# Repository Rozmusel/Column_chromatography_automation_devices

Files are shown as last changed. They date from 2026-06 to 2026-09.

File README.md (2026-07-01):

# Устройства автоматизации колоночной хроматографии
В настоящее время, хроматографический метод разделения веществ широко применим во многих научных лабораториях по всему миру. Одним из наиболее популярных видов является препаративная колоночная хроматография, активно использующаяся исследователями в области органической химии по сей день.
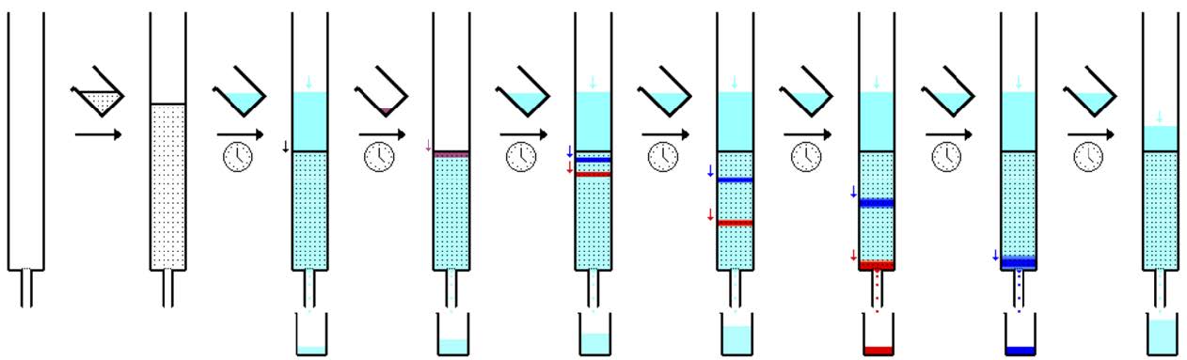
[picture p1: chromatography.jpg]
A1-4CCH

Интерес к данному методу выделения индивидуальных соединений из смеси не случаен – для его проведения нужны крайне дешевые расходные материалы (чаще всего силикагель или цеолит в качестве неподвижной фазы и этилацетат, гексан в качестве элюента) и недорогое стеклянное оборудование (колонка, пробирки или плоскодонные колбы). Более того, в результате прохождения смеси через колонку на выходе научный сотрудник получает продукт с чистотой до 99%.
Подбирая колонку нужного диаметра и регулируя толщину слоя твёрдого адсорбента, исследователь имеет возможность разделять смеси самой различной массы, что является важным преимуществом перед дорогостоящим оборудованием высокоэффективной жидкостной хроматографией (ВЭЖХ), в котором имеются ограничения по массе вводимого вещества. 
Однако существенным недостатком метода препаративной колоночной хроматографии является его длительное время проведение и непосредственное участие исследователя для замены заполненной колбы на пустую под колонкой. В зависимости от диаметра колонки и адсорбента каждая колба наполняется элюентом в среднем за 4-5 минуты, после чего её нужно менять вручную на новую. Так, научный сотрудник вынужден, откладывая проведение синтезов, следить за хроматографическим процессом.
Решением проблемы долгой ручной сортировки может стать устройство, которое умеет вовремя сменять колбы по мере их наполнения и желательно разделять по стекаемо фазе. Так как в лабораториях часто используют конические колбы объёмом 25 мл и 50 мл, то прибор должен уметь работать с ними.

Существующие решения весьма дорогие, потому исследовательские команды часто не могут позволить себе профессиональные ВЭЖХ или сортировщики фракций, моя задача - найти компромисс между качеством разделяемых смесей, удобством и разумной ценой.

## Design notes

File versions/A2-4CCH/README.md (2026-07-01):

# Прототип A2-4CCH
**Allocator for Column Chromatography v2**

## Назначение
* Решение проблемы небольшой вместимости прошлой версии устройства
* Повышение надёжности

## Статус
В процессе разработки.

## Конструкция
* XY стол на винтовой передаче.
* Привод - JGA25-370 DC gear motor.
* Управление на плате STM32G474CEU6 от WeAct.

## Средства разработки
### CAD
* Компас-3D v24

### Прошивка
* STM32CubeMX
* Visual Studio Code

## Результаты

## Выявленные недостатки

### Материалы

### Эксплуатационные испытания

## Основные выводы

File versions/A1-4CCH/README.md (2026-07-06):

# Прототип A1-4CCH
**Allocator for Column Chromatography v1**
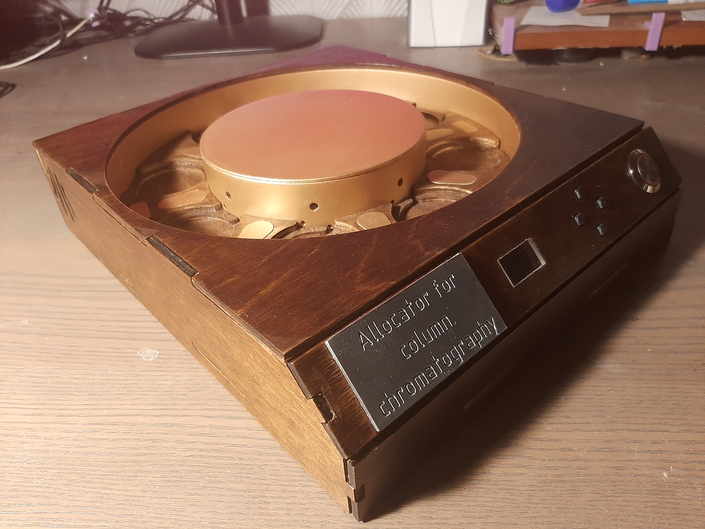
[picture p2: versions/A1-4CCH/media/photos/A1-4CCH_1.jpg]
A1-4CCH

## Назначение
Разработка устройства для автоматической смены колб под хроматографической колонкой по мере их наполнения.
## Статус
Завершён. Испытания проведены.
## Конструкция
* Карусельный механизм для размещения приёмных колб.
* Привод карусели — шаговый двигатель.
* Система управления построена на платформе Arduino.
* Определение наполненности колб лазером и фоторезистором.

## Средства разработки
### CAD
* Autodesk Inventor Professional 2024

### Прошивка
* Arduino IDE

## Результаты
* Разработано и изготовлено работоспособное устройство.
* Работоспособность подтверждена лабораторными испытаниями.
* Продемонстрирована возможность автоматической смены колб по мере их наполнения без участия оператора.
* Получен патент на метод определения наполненности колб.

## Выявленные недостатки
### Конструкция
* Карусельный механизм имеет большие габариты при сравнительно небольшой вместимости.
* Масса и размеры конструкции плохо масштабируются при увеличении количества колб.

### Материалы
* Использование фанеры для изготовления крупных деталей позволило снизить стоимость и ускорить изготовление прототипа, однако оказалось неудачным решением.
* Коробление фанеры приводило к перекосу барабана и ухудшению плавности его вращения.

### Эксплуатационные испытания
* Во время лабораторных испытаний отдельные колбы были пропущены вследствие заедания барабана.
* Маленькая скорость смены колб (возможно попадание капли растворителя мимо колб)
* Нет зациты от растворителя (даже с учётом устойчивости фанеры к растворителям)

## Основные выводы
Карусельная архитектура обладает ограниченной масштабируемостью, а применение фанеры для силовых элементов конструкции отрицательно влияет на надёжность механизма. Основными причинами заеданий являлись недостаточная плавность вращения механизма и геометрические отклонения деталей. Ввиду использования шагового мотора, планетарной передачи и высокого момента на валу из-за отклонений деталей скорость была сильно понижена. Явным недостатком является попадание каплей раствора на рабочую поверхность. Неприятным является факт нахождения колб на значительном возвышении (неудобно устанавливать колонку т.к. она должна быть выше колб т.е. чем ниже колбы тем лучше)

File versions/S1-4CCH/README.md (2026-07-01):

# Прототип S1-4CCH
**Separator for Column Chromatography v1**

## Назначение
* Автоматизация смены колб не только по наполению, но и по смене фазы

## Статус
Запланировано

## Конструкция

## Средства разработки

### Прошивка

## Результаты

## Выявленные недостатки

### Материалы

### Эксплуатационные испытания

## Основные выводы

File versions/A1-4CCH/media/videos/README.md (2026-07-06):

https://disk.yandex.ru/d/LDP9Rj853mVI_g - Лабораторные тесты
https://disk.yandex.ru/d/NLxnKUL3nVSJgw - Видео

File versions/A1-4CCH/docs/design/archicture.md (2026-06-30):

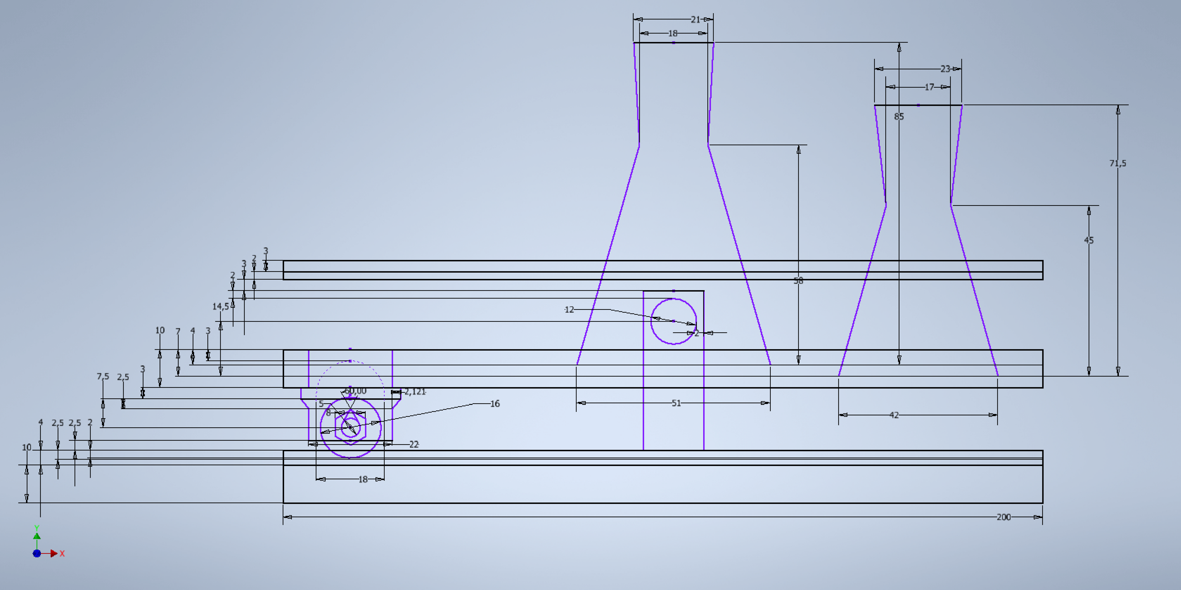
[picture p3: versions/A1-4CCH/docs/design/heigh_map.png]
Карта высот

Толщина нижней основы 10 мм
Толщина верхней основы 4 мм
Углубление для колёс в верхней фанере 2 мм слишком глубокое углубление потребует уменьшение зазора между коробом и основой, уменьшение углубления может сказаться на схождении колёс с углубления
Углубление для вставки стенки 2.5 мм для большей устойчивости
Расстояние от датчика холла до магнита 5 мм, растояние получено приблизительно экспериментально
Расстояние от низа короба до верхней основы 2.5 мм, при такой конфигурации растояние от края окружности до края короба равняется 1 мм
Расстояние от центра окружности до перегородки обусловлено использованием фаски протянувшейся на 2.5 мм по вертикали
Толщина перегородки 3 мм для обеспечения прочности
Лазер расположен на рассоянии 13,5 мм над дном маленькой колбы так как при достижении лазера колба будет заполнена на 15мл а большая будет заполнена на 20мл. С учётом толщины дна колбы расстояние от нижнего держателя до лазера равна 14.5 мм

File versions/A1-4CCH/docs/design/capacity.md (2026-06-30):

Преймущество использования конических колб:
1) устойчивые для работы на поверхности
2) имеют большой объём
3) один из самых популярных видов колб
4) в отличии от цилиндрических колб не требуют установки лазера под угом, что упрощает строение установки и позиционирование колбы относительно лазера.

Угол наклона стенок колб с объёмом:
25мл примерно 74,54 градусов
50мл примерно 73,21 градусов

Угол наклона лазера когда колба пуста или заполненна вычисляется сложнее, если нужен пришлю с рещением и доказательством (каким могу).

Цилиндрические колбы с жидкостью и без не преломляют луч параллельный горизонту и проходящий через их центр. Это подтверждается законом Снеллиуса.Он гласит n1 x sinA1 = n2 x sinA2 где n1 и n2 это Абсолютный показатель преломления света, а с помощью синусов можно понять градусы угла направления луча.
Так как луч проходит перпендикулярно окружности (через центр) и параллельно горизонту, то со стенкой колбы образуется угол 90 градусов, а с перпендикуляром к стенке 0 градусов. Синус 0 градусов это 0, тоесть sinA1 = 0. Выразим sinA2. sinA2 = (n1 x sinA1)/n2. Подставив значение sinA1 мы узнаем что и sinA2 равен 0, а значит преломления не произошло, причём это не зависит от показателя преломления света, а значит от сред, следовательно невозможно проследить присутствие жидкости в такой системе. Это становится возможным только если лазер будет находиться под некоторым углом к конической колбе (Я не использую этот вариант из-за распостранённости конических колб и из-за более сложной системы позиционирования лазера с системой смены конических колб).

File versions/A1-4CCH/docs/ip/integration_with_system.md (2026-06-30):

Метод используется для определения наполненности колб в отсеках

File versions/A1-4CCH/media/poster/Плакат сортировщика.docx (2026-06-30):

Сортировщик фракций для колоночной хроматографии


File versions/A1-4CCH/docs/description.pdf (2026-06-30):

# Автоматический распределитель фракций для жидкостной хроматографии

# Техническое исполнение

## Общий вид:

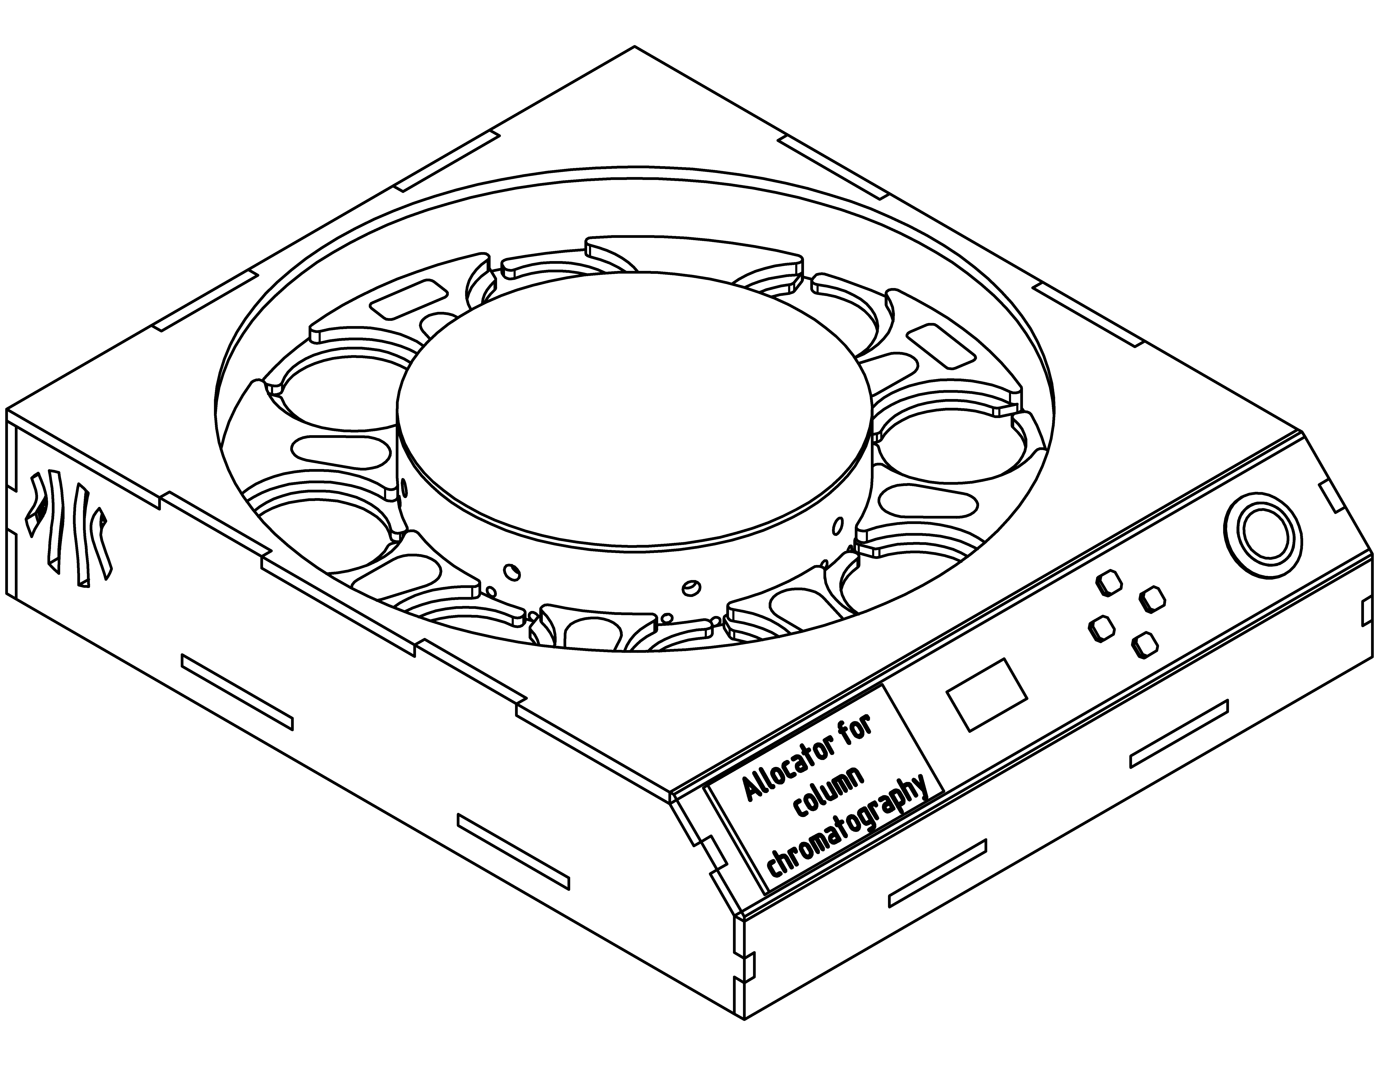
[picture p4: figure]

## Устройство можно разделить на три части: приборная панель, Карусельный

механизм, акустическая система. Рассмотрим в подробности каждую из них.

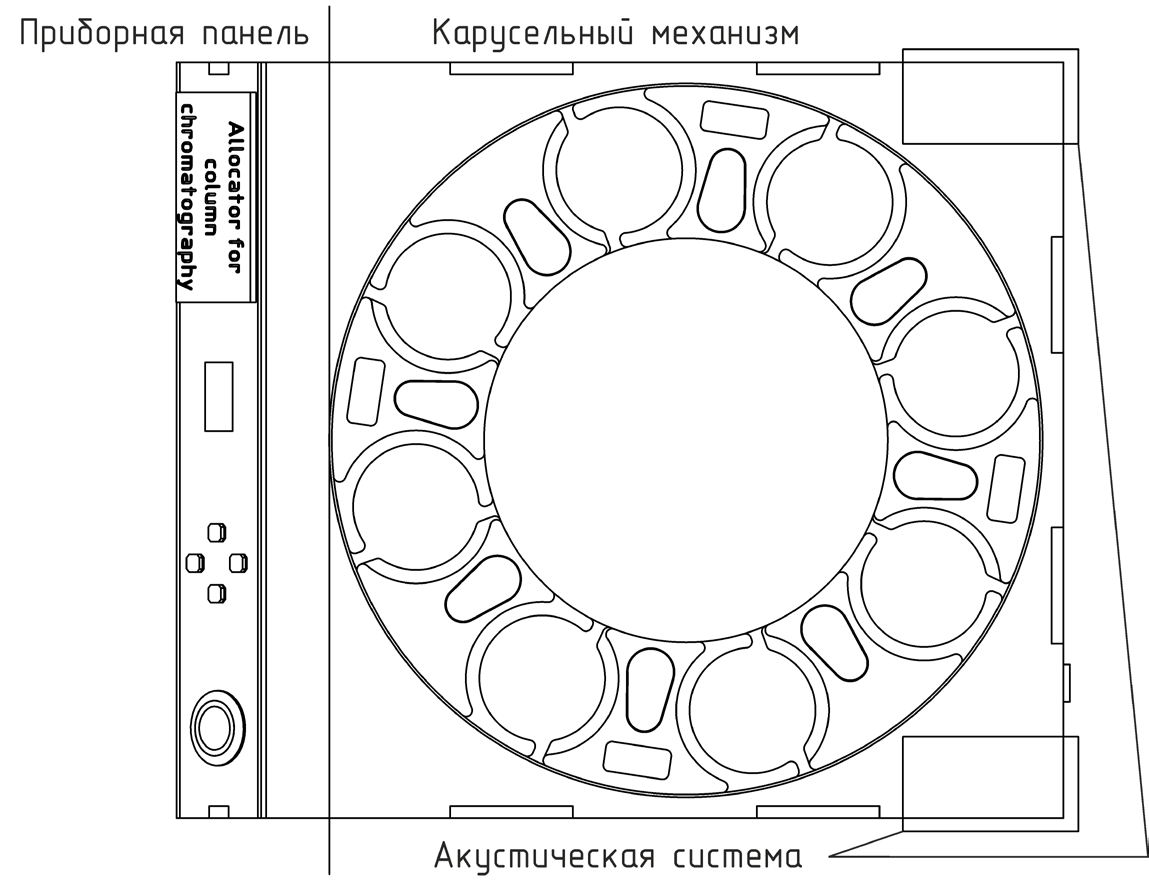
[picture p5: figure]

Приборная панель
На самой приборной панели располагаются сверху в низ: табличка с названием, дисплей под защитным стеклом, четыре кнопки навигации, кнопка включения.

Под приборной панелью располагается плата. Принципиальная схема устройства

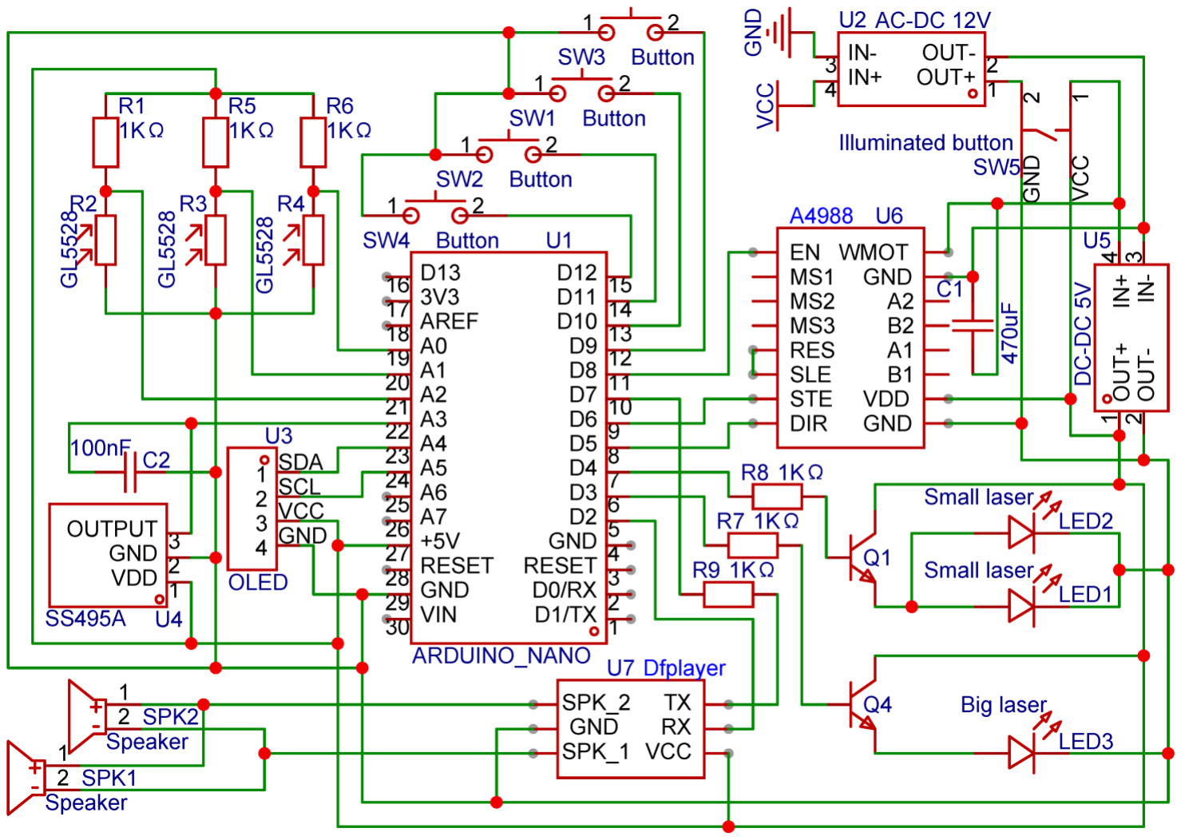
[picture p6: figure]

Где U1 (Arduino nano) отвечает за управление модулями. SW1, SW2, SW3, SW4 – кнопки управления. U2 - внешний блок питания на 12 вольт. SW5 – кнопка включения. U5 – преобразователь на 5 вольт. U6

На плате находятся R1, R5, R6, R7, R8, R9, U1, U5, U6, U7, Q1, Q2, C1, C2. Остальные модули выведены за пределы платы. Под приборной панелью также находятся R2, R3, R4. Они находятся за данными отверстиями.

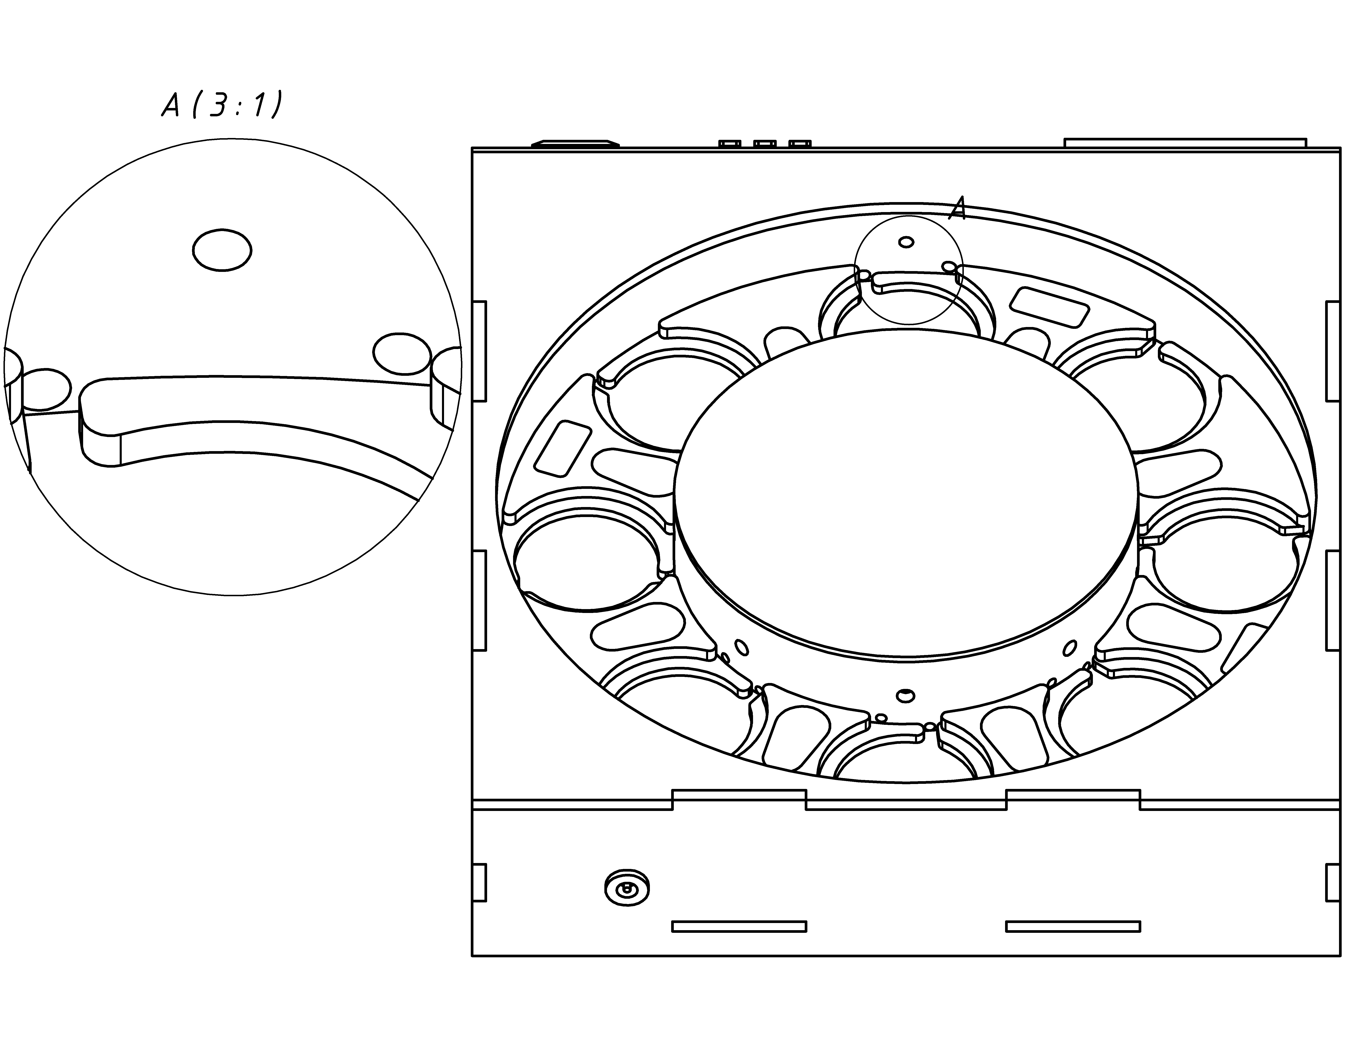
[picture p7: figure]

Карусельный механизм

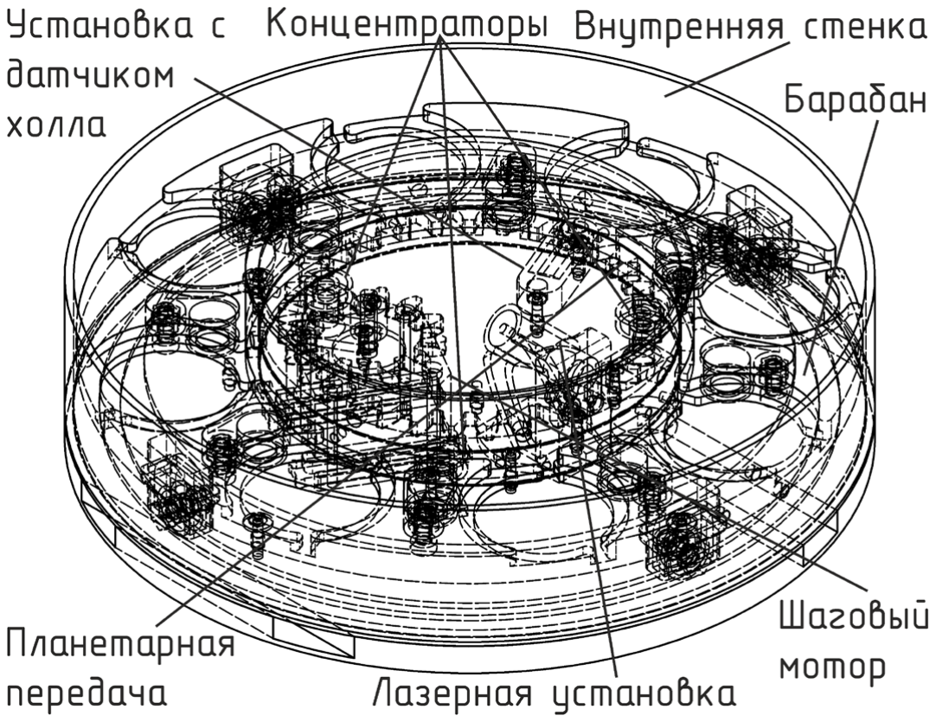
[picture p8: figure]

Состоит из барабана, внутренней стенки, лазерной установки, установки с датчиком холла, трёх концентраторов, шагового мотора и планетарной передачи.

Лазерная установка

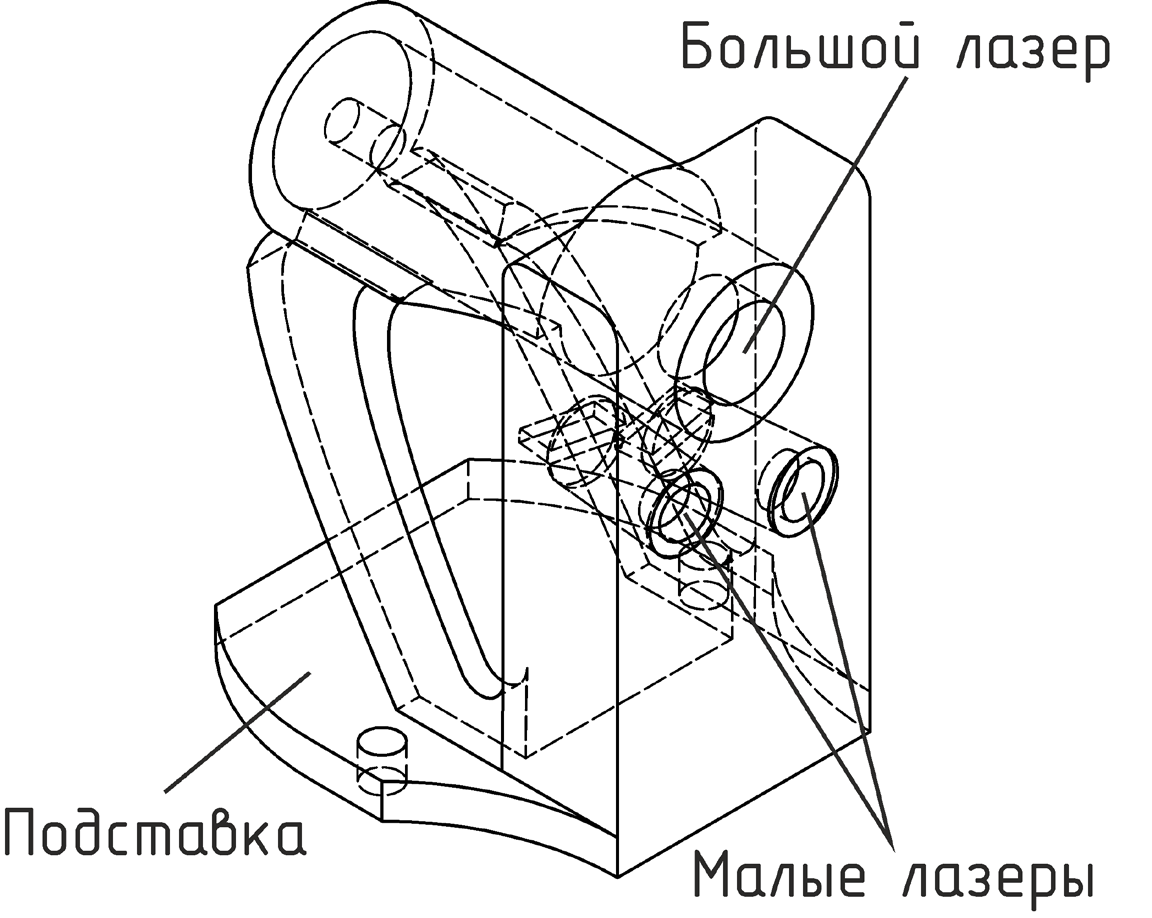
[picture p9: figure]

Состоит из подставки под лазеры, большого лазера, двух малых лазеров. Лазеры направлены на три фоторезистора (отмеченных на схеме как R1, R2, R3).
Установка с датчиком холла состоит из датчика холла и держателя.
Концентратор состоит из подшипника, и держателя.
Планетарная передача состоит из двух шестерней, одна из которых закреплена на валу шагового мотора, а другая внутри барабана.
Барабан
Вид сверху

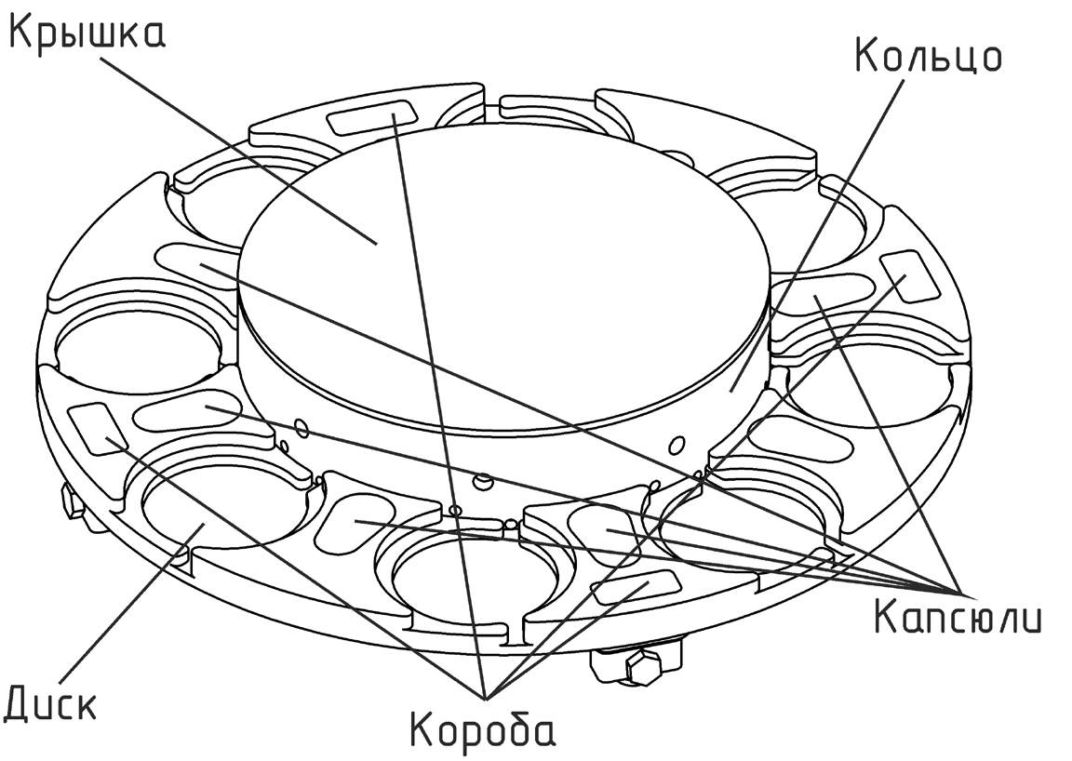
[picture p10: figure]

Вид снизу

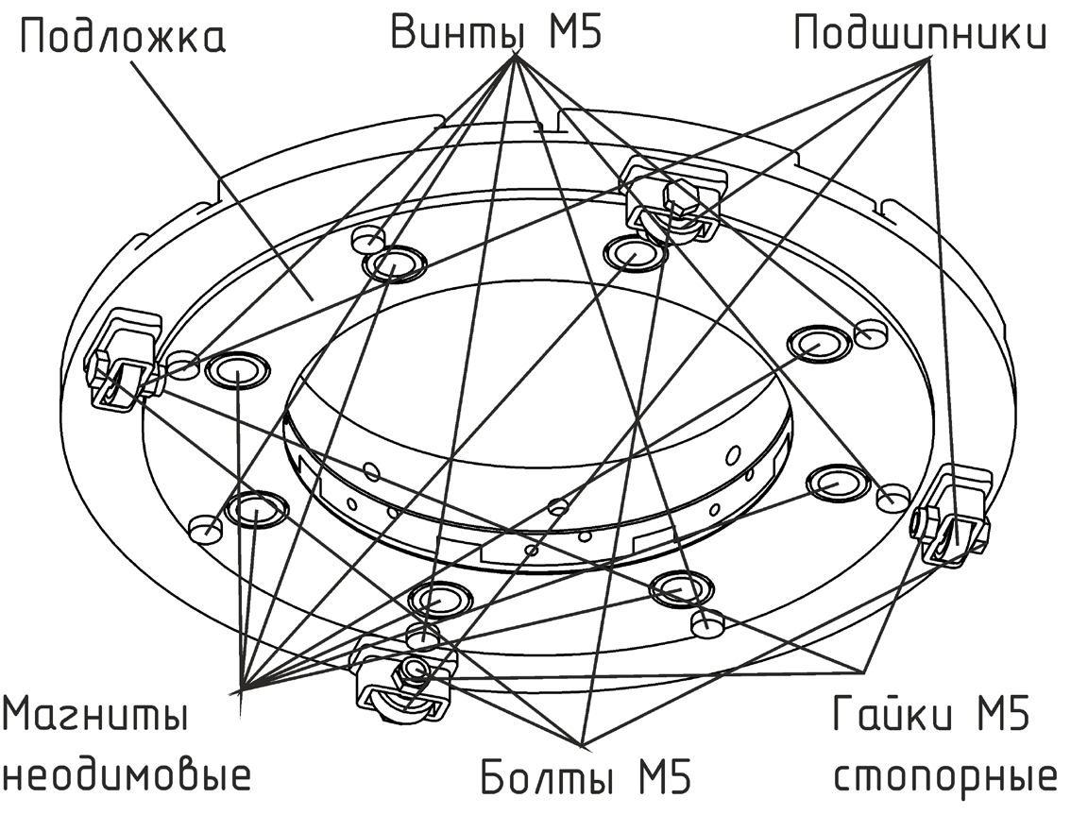
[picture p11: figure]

Барабан состоит из диска, кольца, подложки, четырёх коробов, четырёх болтов М5, четырёх стопорных гаек М5, четырёх подшипников, восьми капсюлей, восьми винтов М5, восьми неодимовых магнитов

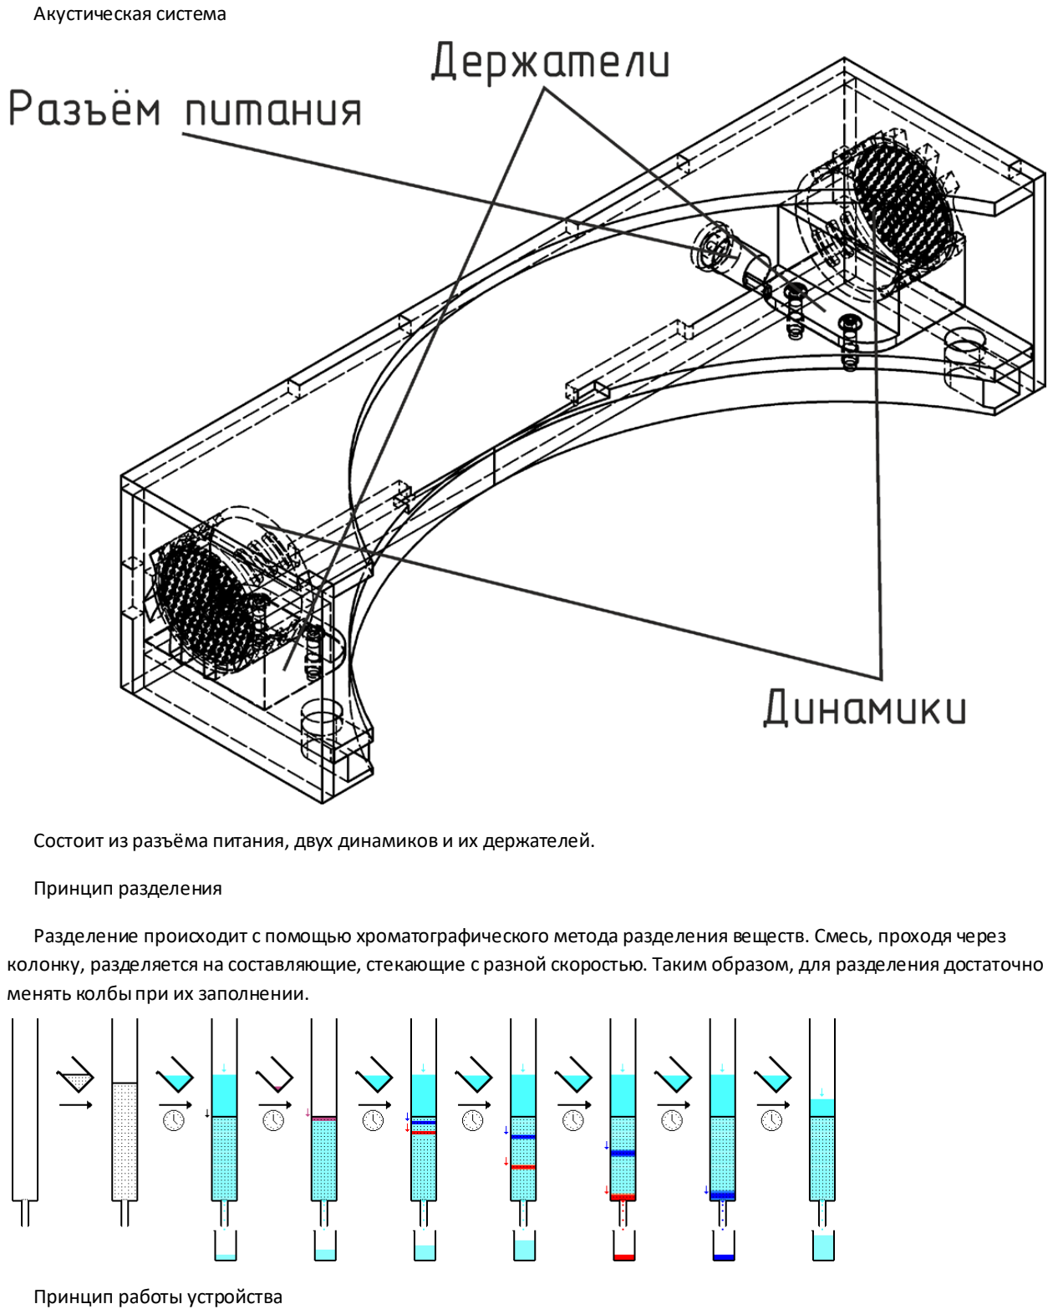
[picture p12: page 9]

Акустическая система

Состоит из разъёма питания, двух динамиков и их держателей.
Принцип разделения
Разделение происходит с помощью хроматографического метода разделения веществ. Смесь, проходя через колонку, разделяется на составляющие, стекающие с разной скоростью. Таким образом, для разделения достаточно менять колбы при их заполнении.

Принцип работы устройства

После включения режима сортировки происходит поиск колбы. После нахождения колбы происходит отслеживание наполненности колбы и по наполнении происходит поиск новой незаполненной. Когда все колбы

Шаговый мотор начинает вращение до момента обнаружения фоторезистором напротив большого лазера его луча, что означает нахождение пустой колбы. С помощью лучей двух малых лазеров происходит определение типа колбы, затем начинается отслеживание превышения уровнем жидкости луча большого лазера, после превышения происходит расчет оставшегося времени до заполнения на основе времени с начала заполнения. После заполнения происходит поиск новой колбы, если не были пройдены все отсеки. Прохождение всех отсеков отслеживается через датчик холла следящего за магнитами. Шаговый мотор передаёт вращение на барабан через планетарную передачу. Чтобы барабан крутился вокруг оси оz, не смещаясь,
Инструкция работы с устройством
В отсеки на диске барабана устанавливаются колбы (устанавливать можно колбы объёмом как 25 мл так и 50 мл в зависимости от предпочтений пользователя)

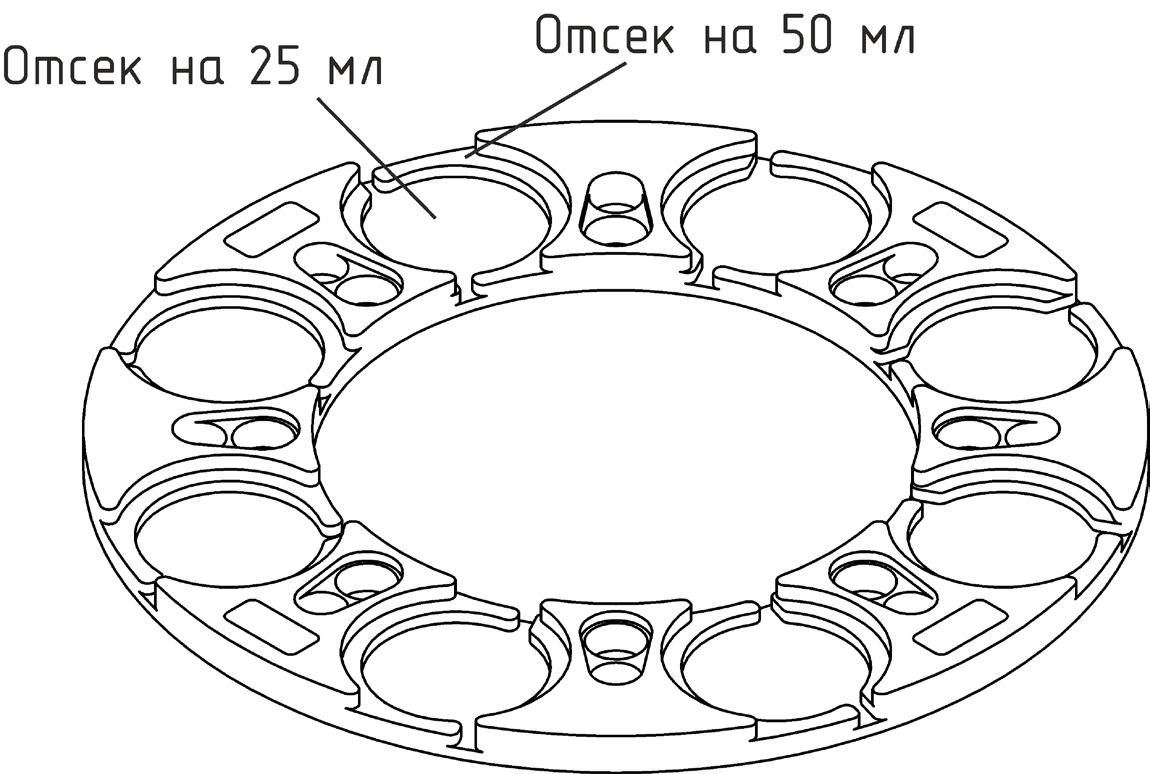
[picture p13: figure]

Затем над колбой, что стоит напротив трёх лазеров, устанавливается колонка с закрытым клапаном. После запуска устройства начинается отслеживание превышение уровня заполнения (которое может установить пользователь в настройках), по заполнении колбы, она сменяется на следующую незаполненную. При заполнении всех колб издаётся предупреждающий сигнал.

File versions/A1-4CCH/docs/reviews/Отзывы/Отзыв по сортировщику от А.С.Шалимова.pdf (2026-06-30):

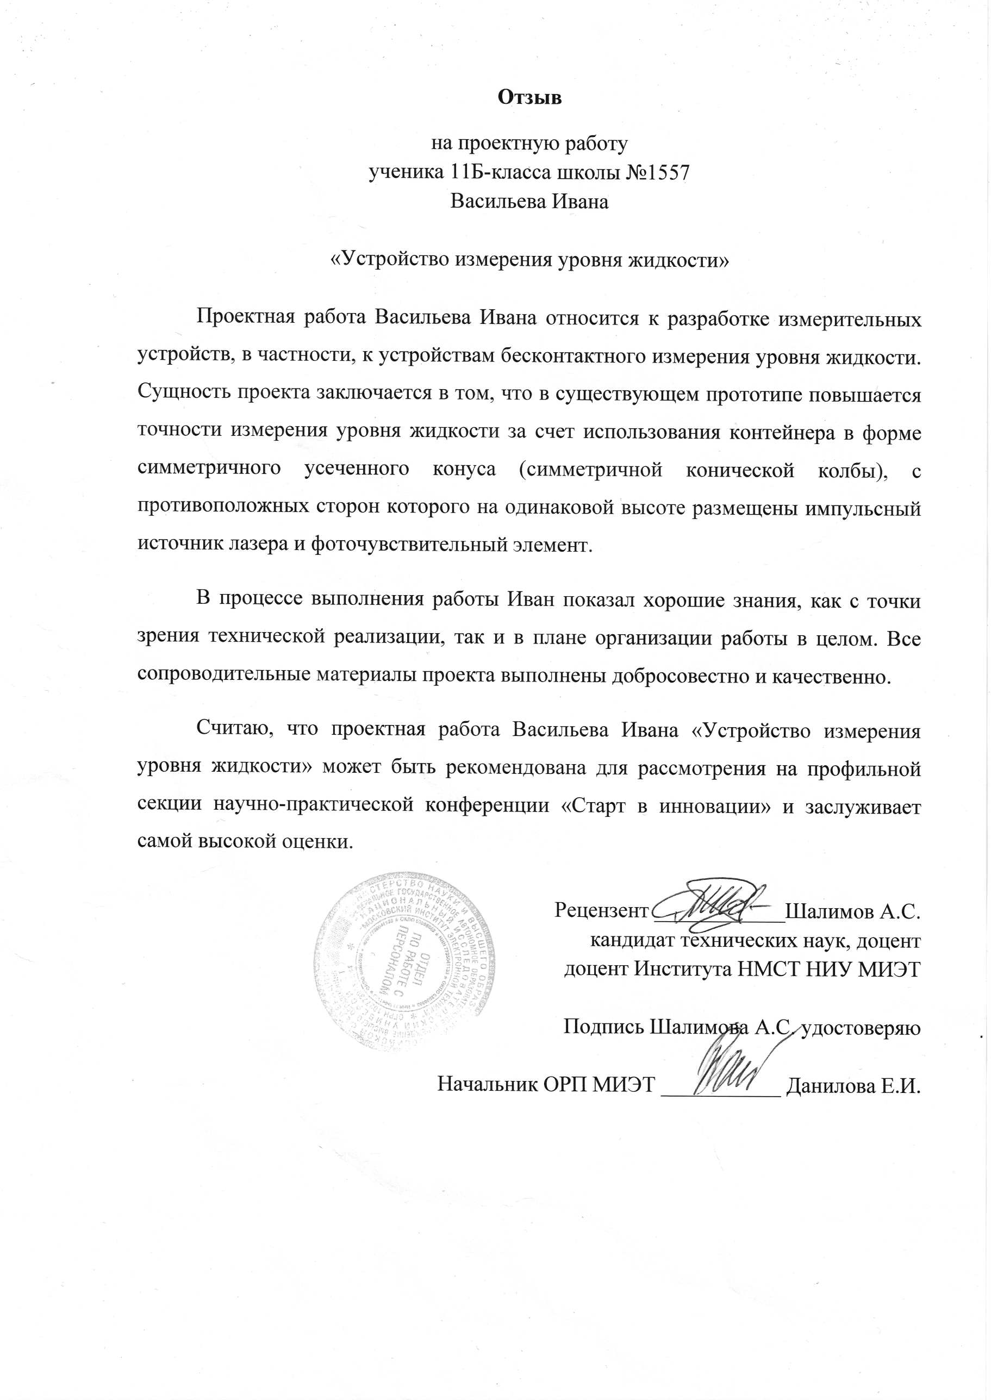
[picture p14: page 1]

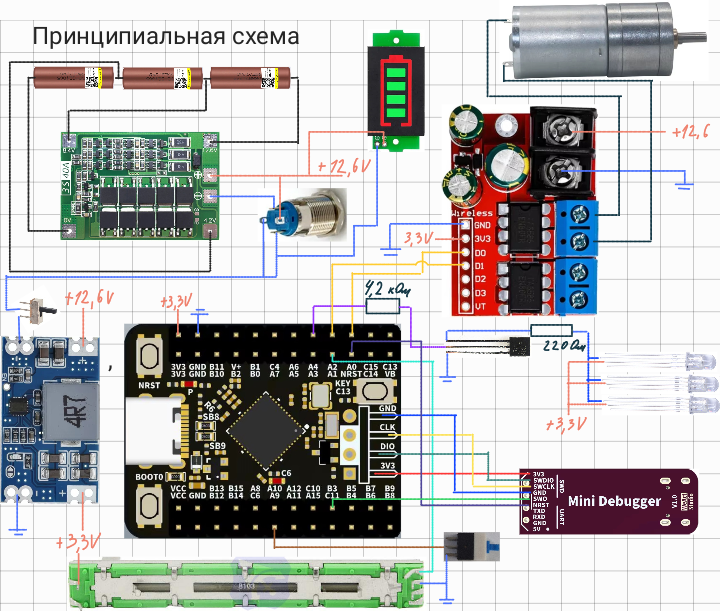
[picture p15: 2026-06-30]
versions/A2-4CCH/experiments/Pivot axis v1.0/electronics/scheme.png

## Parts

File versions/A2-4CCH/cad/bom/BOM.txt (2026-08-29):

Печать					Фил.	Шт.	Статус
Переходник большой оси			PP	x1	Исправить
Подложка переходника			PP	x2	Модель
Переходник большой оси с винтом		PP	x1	Модель
Переходник малой оси			PP	x1	Исправить
Переходник малой оси с винтом		PP	x1	Модель
Кассетница				PP	x1	Модель
Блок					PP	x1	Модель
Крючок					PP	x1	Модель
Вешалка датчика холла с малой оси	PP	x1	Модель
Вешалка датчика холла с большой оси	PP	x1	Отсутствует
Заглушка				PP	x1	Отсутствует
Подшипниковый узел			PP	x1	Модель
Моторный узел				PP	x1	Исправить
Вешалка правая				PP	x1	Модель
Вешалка левая				PP	x1	Модель
Колесо					Nylon	x1	Модель
Шестерня				Nylon	x1	Модель
Стойка					ABS	x1	Модель
Стойка прямого лазера			ABS	x1	Исправить
Стойка углового лазера			ABS	x1	Исправить
Стойка прямого фотодиода		ABS	x1	Отсутствует
Стойка углового фотодиода		ABS	x1	Отсутствует
Стойка платы				ABS	x1	Отсутствует
Стойка ик светодиода			PP	x1	Отсутствует
Стойка ик фотодиода			PP	x1	Отсутствует
Набор направляющих сверления профилей	ABS	x1	Отсутствует

Каркас			Резьба	Отверстия
Профиль 20x20 260мм	x2	x0		x2	-
Профиль 20x20 120мм	x0	x2		x2	-
Профиль 20x20 290мм	x2	x1		x2	-
Профиль 20x20 65мм	x1	x1		x4	-
Профиль 20x20 150мм	x0	x2		x4	-
Профиль 20x20 290мм	x2	x0		x2	-
V-Slot 20x20мм 500мм				x3+1	Доставка

ЧПУ комплектующие				Шт.	Статус
MGN15 rail 120mm				x2	Доставка
MGN15 rail 260mm				x2	Доставка
MGN15C						x4	Доставка
TR8x8 nut					x4	Доставка
Трапецеидальный винт TR8x8 250мм 		x1	-
Трапецеидальный винт TR8x8 110мм		x1	-
Трапецеидальный винт TR8x8 300мм		x2	Доставка
Муфта D20L25 4x6				x1	Доставка
JGA25-370					x2+1	Доставка
Bearing 626-ZZ					x3+1	Доставка

Крепежи
Сухарь пазовый М5				x7	Готов
Сухарь пазовый М3				x10	Готов
Винт М5x10					x26+6	Корзина
Винт М3x25					x8+6	Корзина
Винт М3x10					x10+6	Корзина
Болт М6x20					x2+2	Корзина
Винт М3x6					x8+4	Корзина
Гайка барашковая М6				x2+2	Корзина
Винт с потайной головкой М3x12			x2+2	Корзина
Винт с потайной головкой М3x8			x4+4	Корзина
Винт с потайной головкой М5x16			x4+4	Корзина
Шайба 6х12х1 мм DIN 988				x1+9	Корзина
Винт установочный М4x5				x1+2	Корзина
Винт установочный М3x4				x1+2	Корзина
Вплавляемые гайки М3xD4.6xL3.8			x14	Готов

Модули\датчики
Датчик холла HLD-20				x2+1	Доставка
Лазер						x2+2	Доставка
Фотодиод BPW34					x3+2	Доставка
ИК светодиод TSAL6100				x1+4	Доставка

Электроника
Плата WeAct STM32G474CEU6			х1	Готов
USB-модуль для отладки STM32 WeAct STLink V2.1	х1	Готов
Драйвер TB6612FNG				x1+1	Доставка
Понижающий преобразователь mini560 3.3V		x1+1	Доставка
Разъём DC099 5.5*2.5				x1	Готов
2,8-дюймовый TFT-дисплей ILI9341 SPI		x1	Доставка
OPA381						x3+2	Корзина
Латунные стойки					x4	Готов

Филамент		Вес
Nylon (PA12)		450г			x1	Корзина
PP-GF30			600г			x1	Корзина
ABS			-			x1	Готов

Другое
Брусок ст3 10x10				x1	Доставка
БП 12V 2A					x1	Корзина

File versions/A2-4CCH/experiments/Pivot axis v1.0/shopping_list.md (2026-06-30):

# Покупные
Рельса MGN15					х1	н
Каретка MGN15					х1	н
Конструкционный профиль 20х20 450мм		х1
Сухарь пазовый М3 А131, паз 6			х3
Винт Tr8x8 четырёхзаходный 360мм		х1	н
Латунная гайка Tr8x8 четырёхзаходная		х1	н
Подшипник 608 2RS				х2
Винт с шестигранной головкой М3х8		х4+4
Винт с шестигранной головкой М2,5х10		х2	замена позиции на М3х8 (но лучше поищи у себя 10мм может есть)
Шкив GT2-60T М8 6мм				х1	н
JGA25-370					х1	н
Шкив GT2-20T М4 6мм				х1	н
Внутренний угловой соединитель 6-А, паз 6, H19	х2
Винт установочный М5х5				х4
Ремень GT2-200mm				х1
Винт с потайной шестигранной головкой М3х6	х2
Сухарь пазовый М5, А133, паз 6			х16
Конструкционный профиль 20х40 100мм		х1
Винт с шестигранной головкой М5х8		х16+2
Винт с шестигранной головкой М3х10		х3
Понижающий преобразователь mini560 3.3V		х1	н
Плата WeAct STM32G474CEU6			х1	н
USB-модуль для отладки STM32 WeAct STLink V2.1	х1	н
3S 40A PCB BMS Protection Board			х1	н
Литий-ионная батарея 18650			х3	н
Ячейка на три батареи				х1	н
Винт с шестигранной головкой М4х12		х2
Винт с шестигранной головкой М2х6		х2
Гайка М3					х4
Гайка М2					х2
Гайка М4					х2
Индикатор заряда				х1	н
Переключатель с подсветкой 12мм			х1	н
Драйвер для двух моторов на TA6586		х1	н
Металлический разъем питания DC099 5.5*2.5	х2	н
блок питания 12V 10A 5.5*2.5			х1	н
Провод с разъёмом DC099 5.5*2.5			х1	н
Зарядка для литиевых батарей			х1	н
Потенциометр линейный 10 кОм			х1	н
Кнопка тактовая					х1	н
Переключатель					х1	н
Светодиод					х3	н
Резистор 1,5 кОм				х1	н
Резистор 220 Ом					х1	н
Резистор 60 Ом					х1	н
Транзистор BC337				х1	н
Винт с шестигранной головкой М3х12		х4
Стойки шестигранные М3х4			х8	н

# Печатные
Каретка						х1	б
Ячейка						х1	н
Крепление мотора				х1	н
Стойка подшипника				х2	нп
Стойка						х1	б
Корпус						х1
Скоба						х1	н

н - в наличии, б - бракованная, п - проверка

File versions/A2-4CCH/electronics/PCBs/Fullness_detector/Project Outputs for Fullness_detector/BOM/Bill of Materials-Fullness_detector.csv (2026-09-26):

Designator | Value | PartNumber | Comment | Footprint | Quantity
C1 | 6.8pF | CC0805KRX7R7BB104 | Ceramic capacitor, 6.8pF, X7R, ±10%, 16V, 0805, -55...+125°C | CAP: 0805 | 1
C2 | 1?F | CC0805KRX7R7BB104 | Ceramic capacitor, 1?F, X7R, ±10%, 16V, 0805, -55...+125°C | CAP: 0805 | 1
C5 | 0.1?F | CC0805KRX7R7BB104 | Ceramic capacitor, 0.1?F, X7R, ±10%, 16V, 0805, -55...+125°C | CAP: 0805 | 1
D1 |  | BPW34 | BPW34 | DIO_BPW34 | 1
R1 | 1.2M | RC0805JR-07100RL | Resistor film, 1.2M, ±5%, 0805, 0.125W, -55...+125°C | RES: 0805 | 1
R2 | 12k | RC0805JR-07100RL | Resistor film, 12k, ±5%, 0805, 0.125W, -55...+125°C | RES: 0805 | 1
R3 | 390R | RC0805JR-07100RL | Resistor film, 390R, ±5%, 0805, 0.125W, -55...+125°C | RES: 0805 | 1
U1 |  | OPA381 | OPA381AIDGKR | SOP65P490X110-8N | 1
X1 |  | PLS-3R | Connector, 3pin, 2.54mm, 500VAC, 3A | CON: PLS-3R | 1

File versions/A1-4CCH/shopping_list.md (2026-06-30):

# ЭЛЕКТРОНИКА
Ардуино 1+1				1
Питание 1				2
Припой 1				2
Паечная плата 1+2			1
Разъём управляющий 2 пина 4+8		2
Разъём управляющий 3 пина 2+4		2
Разъём управляющий 4 пина 3+6		2
Резистор 1КОм 5+5			2
Конденсатор 100нф 1+2			2
Конденсатор 470мкф 1+2			2
Драйвер с радиатором 1+2		1
Преобразователь 1+2			1
Плеер 1+2				1
Провод силовой 				2
Маленькая кнопка 4+4			2
Болшая кнопка 1+1			1
Дисплей 1+1				1
Динамик 2+2				1
Разъём питания 1+1			2
Гнездо c8 1+2				0
Кабель c8 1+1				0
Мотор шаговый 1+1			1
Лазер большой 1+2			1
Лазер маленький 2+4			2
Датчик холла 1+3			2
Microsd карта 1+1			2
Транзистор irf520n 1+2			2
Транзистор bc337 2+3			2
Соленоид 1+1				2
Пины 					2

# ДЕТАЛИ
Подшипники 7+3				2
Магнит 8+2				2
Фильтр света 3+3			0
Болт м3 6 мм 3+6			2
Болт м3 12 мм 19+20			2
Болт м3 16 мм 4+4			2
Болт м3 35 мм 4+4			2
Болт м5 10 мм 8+8			2
Болт м5 15 мм 4+4			2
Гайка м3 4+4				2
Гайка м5 стопорная 12+12		2		
Шайба м3 10+10				2
Латуная гайка				2

# ПОКРЫТИЕ
Аэрозольная грунтовка
Аэрозольная краска
Аэрозольный лак
Яхтный лак
Морилка
Шкурка шлифовальная

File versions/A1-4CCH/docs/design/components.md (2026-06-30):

# Барабан
Окружности отсеков колб немного выходят за круг, для того , чтобы можно было сделать красивые загибы.
Расстояние 20 мм между окружностями достаточное для помещения нужных деталей между ними
Капсули ррасположены так, что перпендикуляры от их окружностей к соседним объектам равны, что обеспечивает равное расстояние
Расстояние 103 мм от центра до края короба обеспечивает равноудалённость от соседних объектов
Обод имеет внутренний диаметр 127 мм. При данных значениях стенка обода обладает достаточной толщиной.
Относительно полученного скругления проведены траектории прохождения луча. С учётом его диаметра 4мм создано углубление в нижнем отсеке шириной 4.1 мм, чтобы фреза свободно проходила при фрезеровке

# Короб подшипника
прокаладка для поддержки барабана выступает на 1.5 мм и шириной 3мм
Геометрия короба создана для печати на нижней плоскости
Установлены прижимы для удержания подшипника
Можно регулировать зазорами ширину отверстия под винт ширину и длину корпуса а также толщину прижимов

# Крепежи
Имеют возможность в формулах изменять глубину посадки болта не меняя общую толщину крепежа
Крепежи имеют увеличенные края для того чтобы наносить на них клей

# Луч лазера
Луч маленького лазера имеет диаметр 4 мм, а большого 5 мм

# Шестерни
Модуль шестерёнок равен 3.34
Планетарная шестерня имеет 32 зуба, а маленькая 12
Диаметр штриховой линии у большой шестерни 106.88 мм, а у маленькой 40.08мм

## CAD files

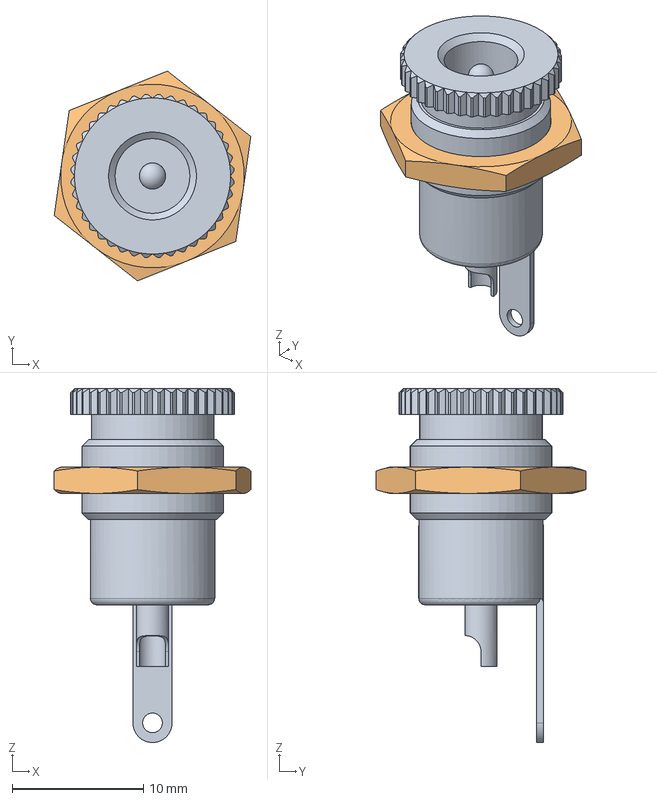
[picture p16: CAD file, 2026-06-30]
versions/A2-4CCH/experiments/Pivot axis v1.0/cad/source/Аккумулятор/DC-099/stp/Con_5.5_Assembly.stp
15.0 x 16.0 x 27.0 mm
DC-Connector 5,5mm female
Nut M11x0.75

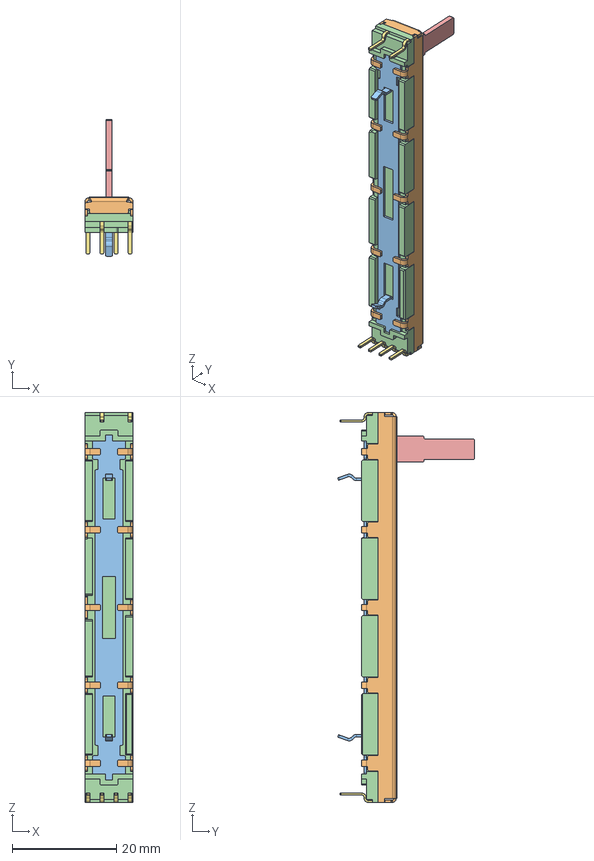
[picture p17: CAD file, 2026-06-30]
versions/A2-4CCH/experiments/Pivot axis v1.0/cad/source/Плата/Линейный потенциометр/stp/linear_potentiometer_b103_asm.stp
9.25 x 26.3 x 75.0 mm
HOUSING
SHIELD
LEVER
DUST_COVER
PIN x 6

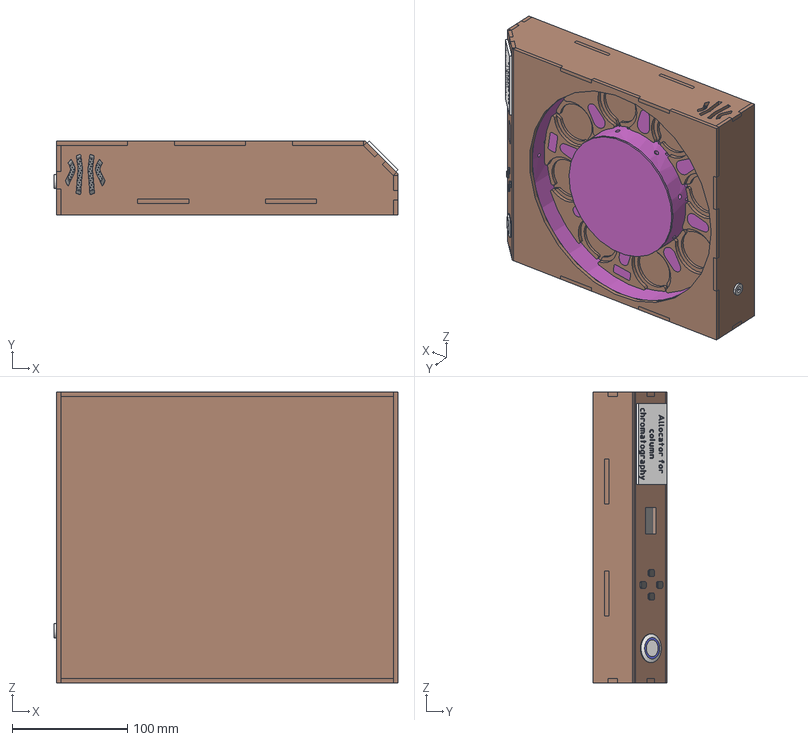
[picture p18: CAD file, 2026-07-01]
versions/A1-4CCH/cad/exports/step/Сборка сортировщика.stp
298.2 x 64.1 x 252.0 mm
Барабан
Капсула x 8
Короб подшипника x 4
Болт x 4
Болт М5 круглый x 8
Гайка М5 стопорная x 12
Подшипник x 7
Магнит x 8
Корпус
Болт М3 x 18
Держатель динамика x 2
Лазерная установка
Установка датчика холла
Концентратор x 3
Мотор
Плата главная
Болт М4 x 4
Болт М3 16 мм x 4
Лазер
Лазер маленький x 2
Internal Gear (32 teeth)
Spur Gear (12 teeth)
Вал
Болт М3 6 мм
Динамик x 2
Табличка
Кнопка
Дисплей
Разъём питания
Шайба М3 x 7
Кнопка маленькая x 4
Окно x 2

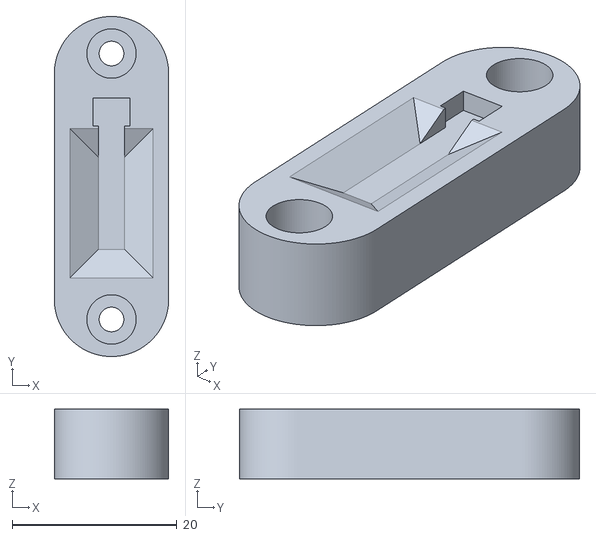
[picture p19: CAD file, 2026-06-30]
versions/A1-4CCH/cad/manufacturing/Печать/Holl_holder.stl
13.9 x 41.3 x 8.50

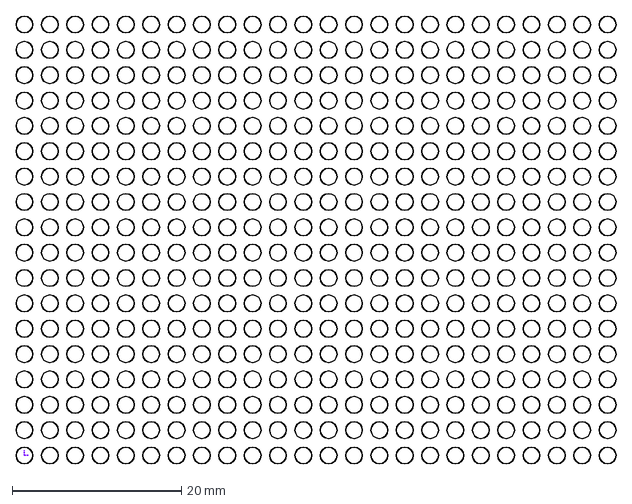
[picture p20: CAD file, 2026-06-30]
versions/A1-4CCH/electronics/plate.dxf
71.0 x 53.0 mm

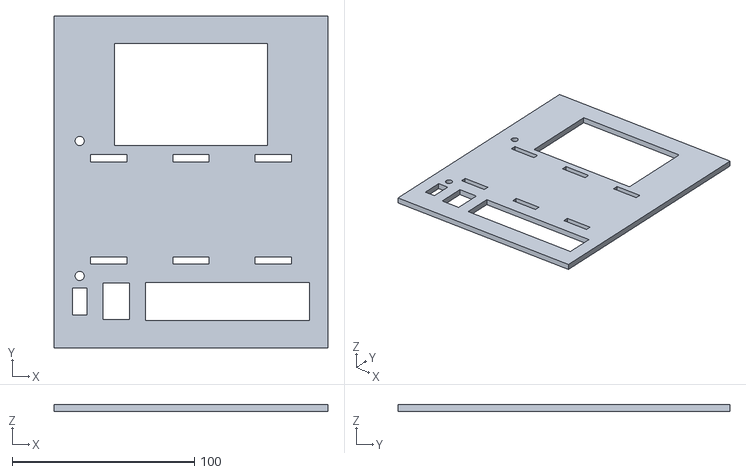
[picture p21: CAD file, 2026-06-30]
versions/A1-4CCH/experiments/device_for_determining_the_fullness_of_a_flask/model/STL/Основание1.stl
150.0 x 182.0 x 4.00

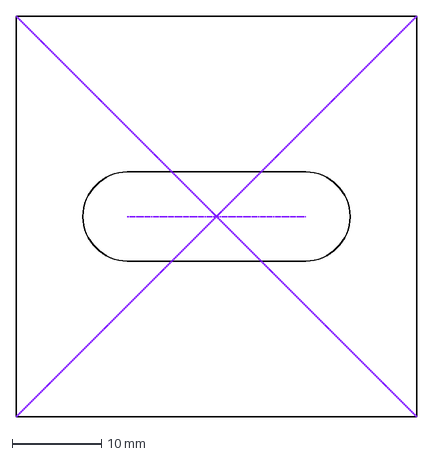
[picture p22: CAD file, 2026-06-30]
versions/A1-4CCH/firmware/bitmaps/Знаки/Минус.dxf
45.0 x 45.0 mm

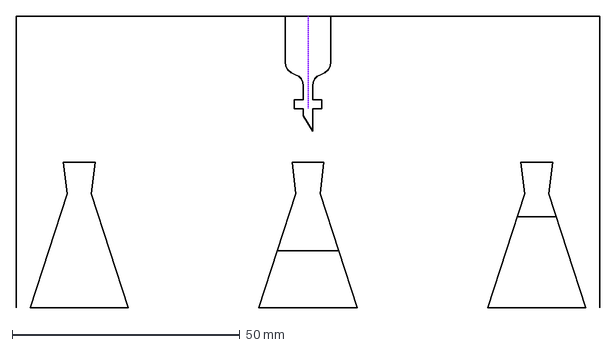
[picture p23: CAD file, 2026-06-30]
versions/A1-4CCH/firmware/bitmaps/Тест анимации/Waiter.dxf
128.0 x 64.0 mm

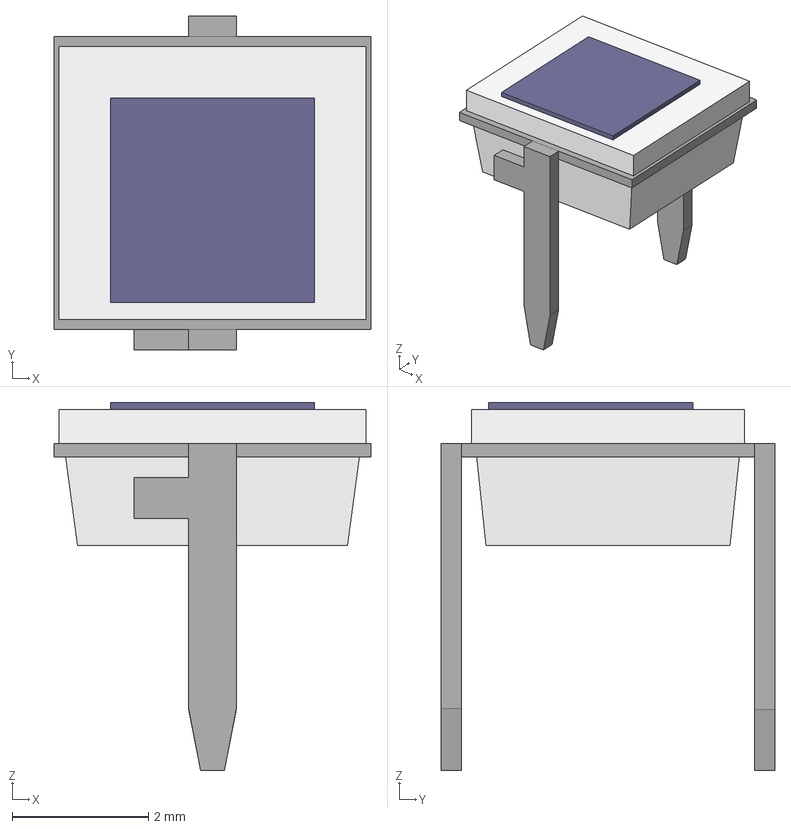
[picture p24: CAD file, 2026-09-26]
versions/A2-4CCH/cad/source/Модули/BWP34/step/BPW34.step
4.65 x 4.90 x 5.40 mm

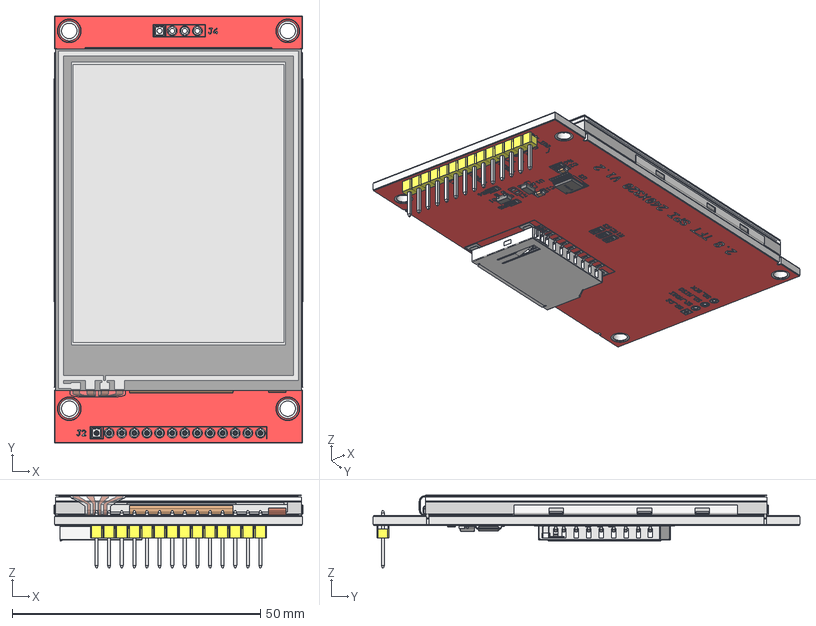
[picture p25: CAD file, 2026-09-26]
versions/A2-4CCH/cad/source/Модули/ILI9341 tft 240x320/step/LCD_MSP2807_fusion.step
50.1 x 86.0 x 14.6 mm
plate and holes
circle001
circle002
circle003
circle004
border001
border002
ShapeString099
ShapeString100
ShapeString102
ShapeString103
cupper_upper
cupper_bottom
mask_bottom
res_silk
res_silk001
res_silk002
res_silk003
res_silk004
res_silk005
cap_silk_up
cap_silk_dwn
cap_silk_up001
cap_silk_dwn001
sot23_left
sot23_right
sot23_left001
sot23_right001
u2_silk002
sd_silk001
line_silk001
line_silk002
ShapeString067
ShapeString105
ShapeString106
ShapeString107
ShapeString108
ShapeString068
ShapeString110
ShapeString111
ShapeString112
ShapeString113
ShapeString069
ShapeString115
ShapeString116
ShapeString117
ShapeString070
ShapeString119
ShapeString120
ShapeString121
ShapeString122
ShapeString071
ShapeString124
ShapeString125
ShapeString126
ShapeString073
ShapeString128
ShapeString129
ShapeString130
ShapeString131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

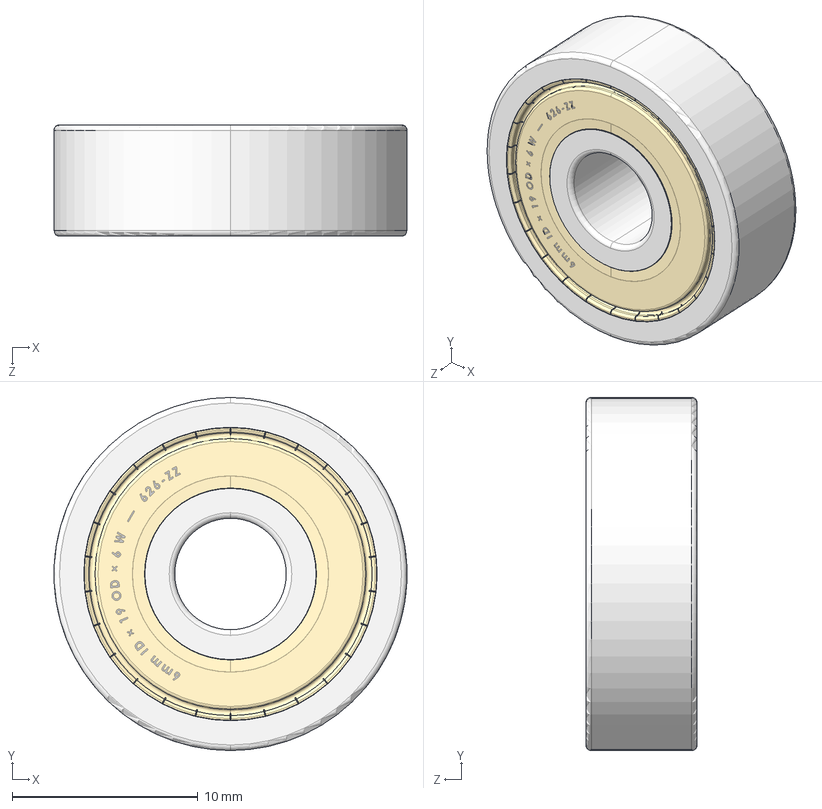
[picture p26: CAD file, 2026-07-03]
versions/A2-4CCH/cad/source/Несущая конструкция/Винтовая передача/step/p BEARING, METRIC 600 MINIATURE SERIES, DOUBLE-SHIELDED 6mm ID × 19 OD × 6 W — 626-ZZ.STEP
19.0 x 19.0 x 6.00 mm

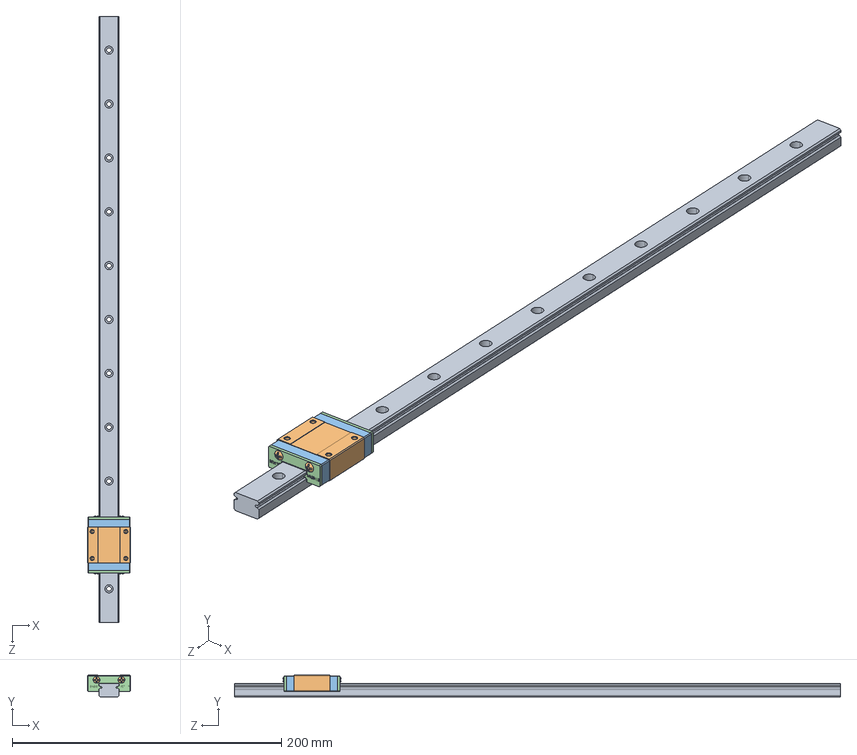
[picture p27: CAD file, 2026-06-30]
versions/A2-4CCH/cad/source/Несущая конструкция/Линейные направляющие/Исходники/MGN15.STEP
32.0 x 16.0 x 450.0 mm
MGNR15R400HM
MGN15_Body
MGN15_EndCap x 2
MGN15_Seal x 2
MGN15_Cage x 2
MGN15_Ball x 26

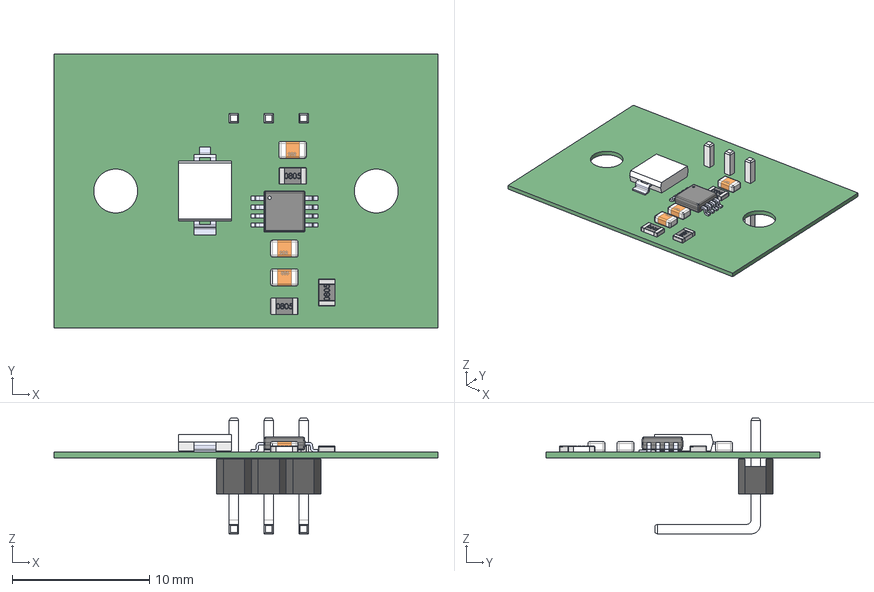
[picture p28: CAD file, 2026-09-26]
versions/A2-4CCH/electronics/PCBs/Fullness_detector/Project Outputs for Fullness_detector/ExportSTEP/detector.step
28.0 x 20.0 x 8.45 mm
User Library-PLS-3R
chip_0805_r x 3
SW3dPS-0805 SMD Capacitor x 3

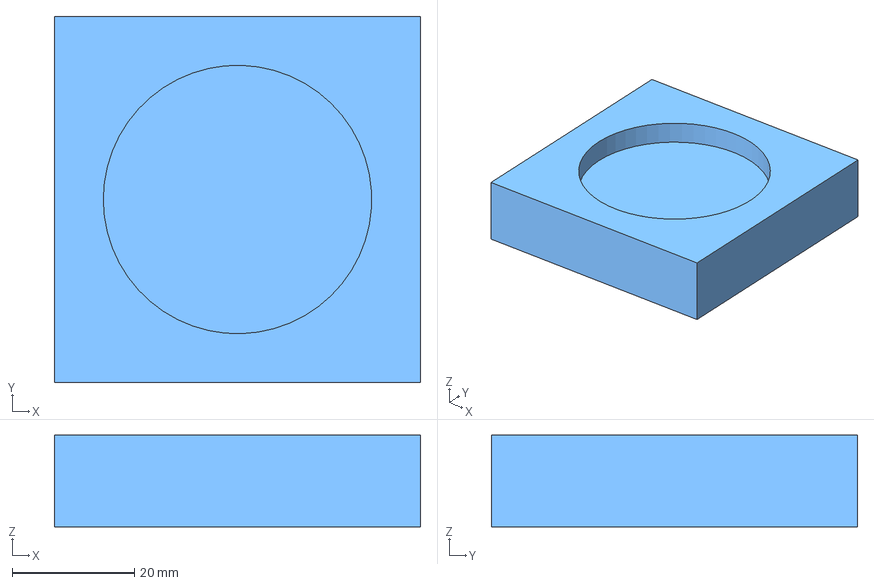
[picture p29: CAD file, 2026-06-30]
versions/A2-4CCH/experiments/Pivot axis v1.0/cad/manufactoring/Ячейка.stp
60.0 x 60.0 x 15.0 mm

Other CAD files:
versions/A2-4CCH/experiments/Pivot axis v1.0/cad/source/Аккумулятор/step/12mm Power Button With LED v1.step
versions/A2-4CCH/experiments/Pivot axis v1.0/cad/source/Аккумулятор/Ячейка/stp/BatteryHolder3S.STEP
versions/A2-4CCH/experiments/Pivot axis v1.0/cad/source/Несущий профиль/step/A131-Sukhar-pazovyy-M3_-paz-6.STEP
versions/A2-4CCH/experiments/Pivot axis v1.0/cad/source/Плата/stp/PCB 70x90mm v1.step
versions/A1-4CCH/cad/manufacturing/Печать/Button_holder.stl
versions/A1-4CCH/cad/manufacturing/Печать/Concentrator.stl
versions/A1-4CCH/cad/manufacturing/Печать/Display_holdel.stl
versions/A1-4CCH/cad/manufacturing/Печать/Kapsule.stl
versions/A1-4CCH/cad/manufacturing/Печать/Korob.stl
versions/A1-4CCH/cad/manufacturing/Печать/Laser_holder.stl
versions/A1-4CCH/cad/manufacturing/Печать/Lid.stl
versions/A1-4CCH/cad/manufacturing/Печать/Plateta.stl
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

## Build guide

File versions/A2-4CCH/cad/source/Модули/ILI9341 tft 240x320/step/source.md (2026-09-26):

https://grabcad.com/library/2-8-inch-tft-lcd-module-1

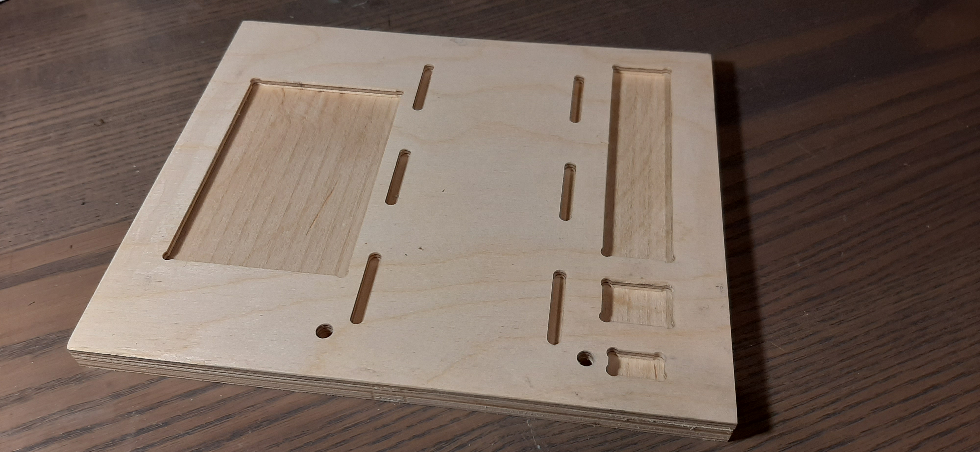
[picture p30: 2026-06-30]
versions/A1-4CCH/experiments/device_for_determining_the_fullness_of_a_flask/assembly/Действие 2.jpg

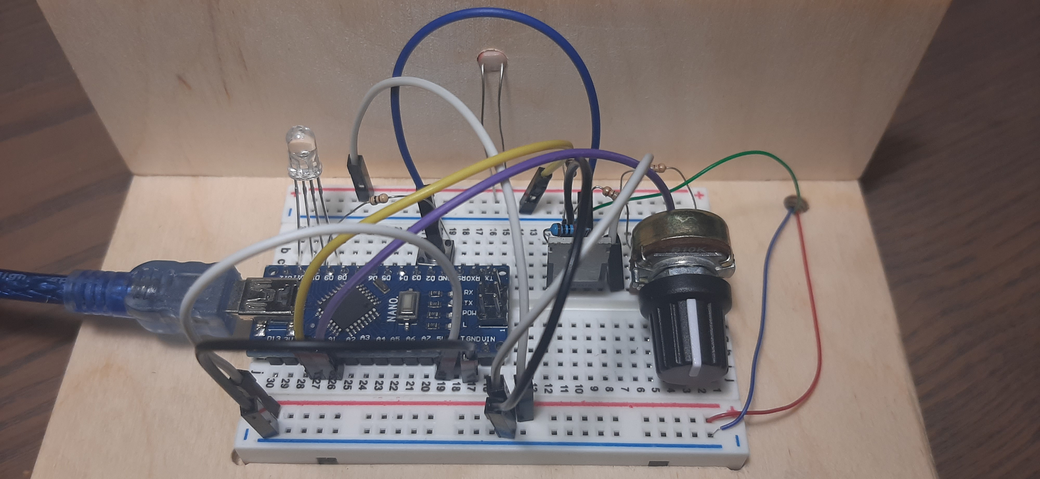
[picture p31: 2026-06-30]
versions/A1-4CCH/experiments/device_for_determining_the_fullness_of_a_flask/assembly/Действие 9.jpg

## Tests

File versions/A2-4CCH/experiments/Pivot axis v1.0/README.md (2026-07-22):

# Эксперимент A2-4CCH
**Pivot axis**
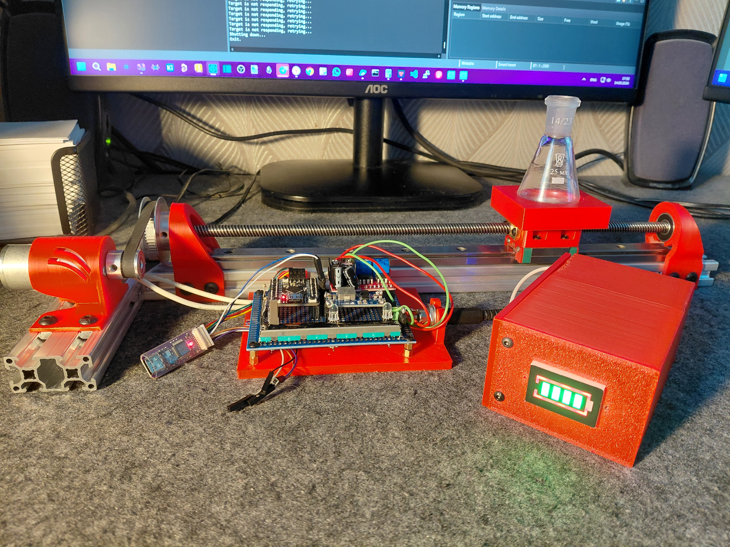
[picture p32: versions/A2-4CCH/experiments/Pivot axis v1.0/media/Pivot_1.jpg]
Pivot

## Назначение
Тестирование передвижения каретки с колбой по оси
## Статус
Завершён. Испытания проведены.
## Конструкция
* Трапецеидальный винт с гайкой Tr8x8.
* Привод - JGA25-370 DC gear motor.
* Управление на плате STM32G474CEU6 от WeAct.
* Управление скоростью и направлением линейным потенциометром.

## Средства разработки
### CAD
* Компас-3D v24

### Прошивка
* CubeIDE 1.18.1

## Результаты
* Реализовано перемещение вдоль оси

## Выявленные недостатки
### Конструкция
* Ременная передача занимает много места.
* Из-за неосведомлённости о необходимости шлифовать ось, посадка подшипника была произведена лишь частично.
* Вместо угловых сухарей стоило использовать blind joint.

### Материалы
* Использование экструзионных профилей сильно облегчило разбработку конструкции

### Эксплуатационные испытания
* Из-за недостатков драйвера наблюдался прерывистый ход на первом канале при движении в одну из сторон, второй канал дал плавность в обе стороны, но был несколько разбалансирован
* Контакт потенциометра отходил при неосторожном передвижении движка, что также сказывалось на плавности хода

## Основные выводы
Необходимо заменить драйвер, шлифовать оси и использовать крепление blind joint.

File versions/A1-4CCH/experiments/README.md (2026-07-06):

В процессе разработки понадобилось протестировать метод определения наполненности колб и изучить зависимость интенсивности света попадающих на фоторезисторы от трёх лазеров (главного для определения наполненности и двух дополнительных для определения типа колбы). Результаты изысканий можно найти в этой папке.

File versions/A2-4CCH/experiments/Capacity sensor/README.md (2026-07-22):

# Эксперимент A2-4CCH
**Pivot axis**
Pivot
## Назначение
Тестирование ёмкостного сенсора FDC1004 и подбор параметров платы
## Статус
В разработке
## Конструкция

## Средства разработки
### CAD
* Компас-3D v24

### Прошивка

## Результаты

## Выявленные недостатки
### Конструкция

### Материалы

### Эксплуатационные испытания

## Основные выводы

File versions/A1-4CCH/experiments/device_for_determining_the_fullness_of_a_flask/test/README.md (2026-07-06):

https://disk.yandex.ru/d/myLf6zYDCNW9NA - Видео

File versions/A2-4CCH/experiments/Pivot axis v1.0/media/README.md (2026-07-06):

https://disk.yandex.ru/d/9fP0QyKBivaYkw - Видео

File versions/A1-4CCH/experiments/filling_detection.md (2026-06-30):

Вращение с колбами
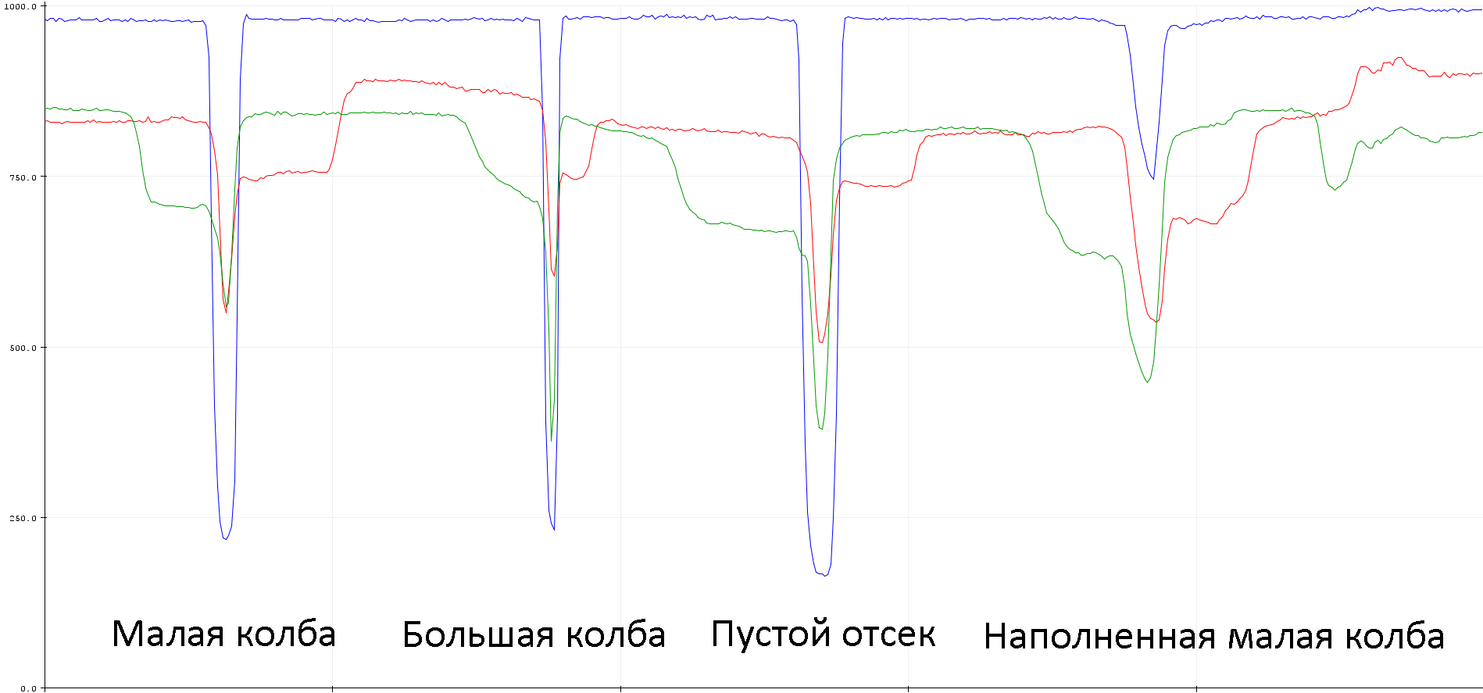
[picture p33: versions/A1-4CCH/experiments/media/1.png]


График с фоторезисторов при вращении вручную без колб
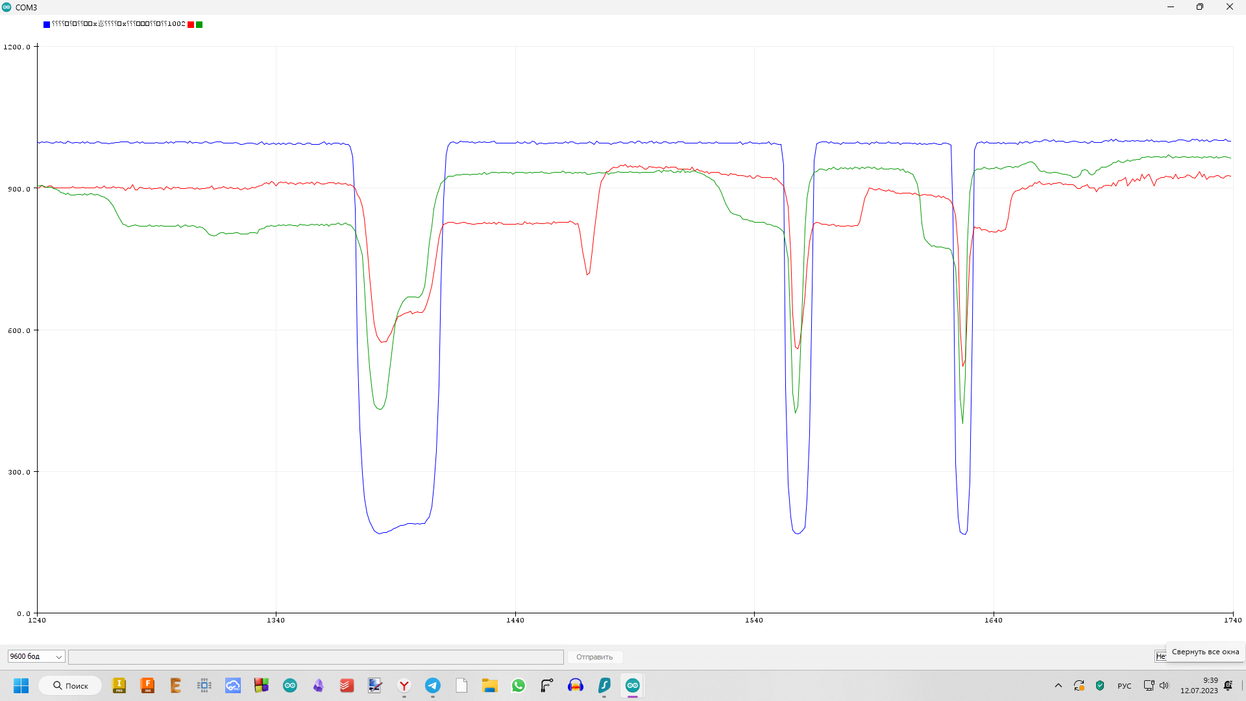
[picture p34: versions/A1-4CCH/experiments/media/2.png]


Фоторезисторы при установке большой колбы вручную
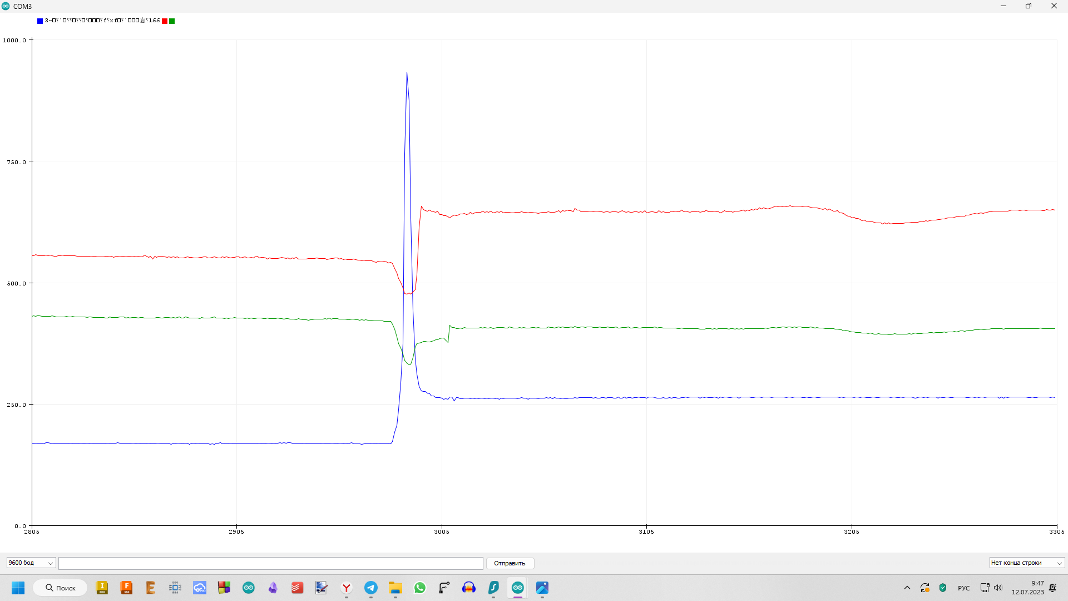
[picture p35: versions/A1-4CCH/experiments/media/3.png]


Фоторезисторы при установке маленькой колбы вручную
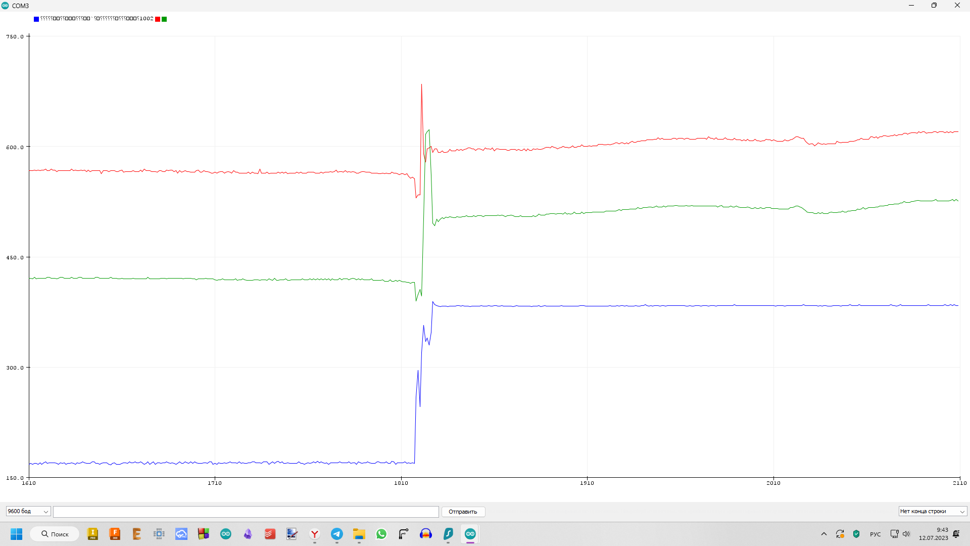
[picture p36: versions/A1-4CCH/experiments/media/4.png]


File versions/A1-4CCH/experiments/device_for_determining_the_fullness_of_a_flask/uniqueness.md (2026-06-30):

Используются дешёвые компоненты (фоторезистор, лазер, резисторы, блок питания. Микроконтроллер можно заменить на компаратор для сравнения напряжений)
Не требуется большая вычислительная мощность (простой алгоритм)
Маленькое энергопотребление (за счёт включения лазера только на протяжении около 250 микросекунд)
Долговечность (В среднем срок службы диодного лазера 15000 часов, срок службы фоторезистора тоже исчисляется тысячами.)
Бесконтактность
Простота
Лазер находится на определённой высоте. Если лазер отклонился можно судить о наличии некоторого фиксированного объёма и более его.
Возможность настройки чувствительности (на моей схеме за это отвечает потенциометр)
Бесшумность
Маленькие размеры
Надёжность
Бесшумность
Быстрота

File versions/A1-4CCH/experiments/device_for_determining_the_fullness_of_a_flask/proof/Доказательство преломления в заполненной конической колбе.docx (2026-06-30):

Преломление луча в конической колбе

Дано:

Луч проходит параллельно плоскости дна колбы и через её ось вращения. Рассмотрим осевое сечение конической колбы. Это с учётом стенок равнобедренная трапеция с ещё одной равнобедренной трапецией внутри первой. Толщина стенки одинаковая. Боковые стороны трапеций параллельны между собой, как и их нижние основания.

a – Перпендикуляр к прямой AB через точку I

b – Перпендикуляр к прямой FE через точку J

c – Перпендикуляр к прямой HG через точку K

d – Перпендикуляр к прямой DC через точку L

n1 – Показатель преломления в воздухе

n2 – Показатель преломления в боросиликатном стекле

n3 – Показатель преломления в жидкости

n1<n3<n2

α1 – Острый угол

β – Углы при нижних основаниях трапеций

I – Точка в которой происходит первое преломление луча при переходе из среды с n1 в среду с n2

J – Точка в которой происходит второе преломление луча при переходе из среды с n2 в среду с n3

K – Точка в которой происходит третье преломление луча при переходе из среды с n3 в среду с n2

L – Точка в которой происходит четвёртое преломление луча при переходе из среды с n2 в среду с n1

M – Точка на луче до преломлений

N – Точка на луче после всех преломлений

Докажем, что:

Луч, выходящий из колбы, направлен вниз.

Доказательство:

Фиг.2 MI находится под углом α1 к прямой a. α1 = 90 - ∠ MIA. ∠ MIA = ∠ IAD так как накрест лежащие при MI ∥ AD (по условию) и секущей IA. ∠ IAD = β ⇒ α1 = 90 – β. По закону Снеллиуса после преломления в точке I, при переходе из среды с n1 в среду с n2 будет выполняться sinα1 * n1 = sinα2 * n2 ⇒ IJ будет под углом α2 к прямой a. Угол между прямой a и IS равен углу между прямой b и отрезком IS так как a ∥ b и IS секущая. По закону Снеллиуса после преломления в точке J, при переходе из среды с n2 в среду с n3 будет выполняться sinα2 * n2 = sinα3 * n3.Выразим n1 и n3. n1 = (sinα2 * n2)/(sinα1) , n3 = (sinα2 * n2)/(sinα3) . Сравним n1 и n3. По условию n1<n3<n2 ⇒ n1<n3 ⇒ (sinα2 * n2)/(sinα1)<(sinα2 * n2)/(sinα3) ⇒ 1/(sinα1)<1/(sinα3) ⇒ sinα3 < sinα1 ⇒ α3 < α1. Пусть угол между JK и прямой c равен α4. Так как EFGH – трапеция, то продолжения EF и HG пресекаются. Пусть EF ∩ HG = T. ∠ ETH = 180 – 2β. Рассмотрим PJTK. ∠ JPK = 360 – 90 – 90 – ∠ ETH = 2β. Пусть b ∩ a = P. Рассмотрим треугольник JPK. ∠ JKP = α4, ∠ JPK = 2β, ∠ KJP = α3. ∠ JKP = α4 = 180 - 2β - α3 = 2 * (90 - β) - α3. Так как α1 = 90 – β, то α4 = 2 * α1 - α3. Так как α3 < α1, то α1 < α4. По закону Снеллиуса после преломления в точке K, при переходе из среды с n3 в среду с n2 будет выполняться sinα4 * n3 = sinα5 * n2. Угол между прямой c и отрезком KL равен углу между прямой d и отрезком KL, так как накрест лежащие при c ∥ d и секущей KL. По закону Снеллиуса после преломления в точке L, при переходе из среды с n2 в среду с n1 будет выполняться sinα5 * n2 = sinα6 * n1. Так как sinα4 * n3 = sinα5 * n2, то sinα4 * n3 = sinα6 * n1. Так как n3<n2 (по условию), то sinα4 < sinα6. Получается, из-за того, что угол между прямой b и отрезком JK меньше угла между прямой b и отрезком MI , часть луча, отмеченная как JK приближается к основанию после преломлений в точках I и J. Угол между отрезком LN и прямой d больше угла между прямой a и отрезком MI ⇒ часть луча, отмеченная как LN, будет отклоняться к стороне AD ⇒ между стенок колбы и после всех преломлений в заполненной колбе луч проходящий через её ось вращения будет направлен вниз. Луч, выходящий из колбы, направлен вниз ч.т.д

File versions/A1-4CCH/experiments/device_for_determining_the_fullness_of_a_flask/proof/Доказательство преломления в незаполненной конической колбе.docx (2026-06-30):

Преломление луча в конической колбе

Дано:

Луч проходит параллельно плоскости дна колбы и через её ось вращения. Рассмотрим осевое сечение конической колбы. Это с учётом стенок равнобедренная трапеция с ещё одной равнобедренной трапецией внутри первой. Толщина стенки одинаковая. Боковые стороны трапеций параллельны между собой, как и их нижние основания.

a – Перпендикуляр к прямой AB через точку I

b – Перпендикуляр к прямой FE через точку J

c – Перпендикуляр к прямой HG через точку K

d – Перпендикуляр к прямой DC через точку L

n1 – Показатель преломления в воздухе

n2 – Показатель преломления в боросиликатном стекле

n1 < n2

α1 – Острый угол

β – Углы при нижних основаниях трапеций

I – Точка в которой происходит первое преломление луча при переходе из среды с n1 в среду с n2

J – Точка в которой происходит второе преломление луча при переходе из среды с n2 в среду с n1

K – Точка в которой происходит третье преломление луча при переходе из среды с n1 в среду с n2

L – Точка в которой происходит четвёртое преломление луча при переходе из среды с n2 в среду с n1

M – Точка на луче до преломлений

N – Точка на луче после всех преломлений

a ∩ FE = S

d ∩ GH = Z

IR – Продолжение отрезка MI

OL – Продолжение отрезка LN

JR – Перпендикуляр к отрезку MI

KO – Перпендикуляр к отрезку LN

Докажем, что:

В пустой конической колбе луч, выходящий из колбы, будет продолжением входящего (будет на той же высоте над дном колбы и параллелен ему)

Доказательство:

А) Фигура1. До преломления часть луча, отмеченная отрезком MI, находится под углом α1 к прямой a в среде с n1. По закону Снеллиуса sinα1 * n1 = sinα2 * n2 после преломления в точке I среда с n1 сменится на среду с n2 следовательно ⇒ sinα1 сменится на sinα2 ⇒ α1 сменится на α2 причём α2 острый угол. Так как a ⊥ AB и b ⊥ EF, а EF ∥ AB (по условию), то a ∥ b. Угол между прямой a и отрезком IJ, так как накрест лежащие при a ∥ b и секущей IJ. Найдём угол между частью луча JK и перпендикуляром b. По закону Снеллиуса sinα2 * n2 = sinα1 * n1 этот угол будет равен sinα1 ⇒ равен α1. Так как отрезки MI и JK имеют угол α1 к a ∥ b соответственно, то MI ∥ JK ⇒ JK ∥ AD. Так как ∠ FEH = ∠ JHE (по условию) и JK ∥ AD, то EJKH равнобедренная трапеция ⇒ ∠ EJK = ∠ HKJ, так как углы при верхнем основании. ∠ MIB вертикален ∠ EJK так как EF ∥ AB (по условию) и MI ∥ JK, то ∠ MIB= ∠ EJK. ∠ MIB = ∠ HKJ, ∠ EJK = ∠ HKJ ⇒ ∠ MIB = ∠ HKJ.Так как ∠ MIB = ∠ HKJ и угол между отрезком JK и перпендикуляром c равен ∠ HKJ - 90 ° и угол между отрезком MI и прямой a равен ∠ MIB - 90 ° равен sinα1 значит угол между отрезком JK и перпендикуляром c равен углу между отрезком MI и перпендикуляром a равен sinα1. Так как в точке K происходит переход из среды с n1 в среду с n2, а в точке L происходит переход из среды с n2 в среду с n1 и угол при отрезке MI и прямой a равен углу при отрезке JK и прямой c, то преломление происходит аналогично преломлению в точках I и J ⇒ угол между прямой c и отрезком KL равен ∠ KLZ равен sinα2, а угол между прямой d и отрезком LN равен sinα1 и JK ∥ LN. JR ⊥ MI (по условию) и MI ∥ JK ⇒ JR ⊥ JK. Аналогично KO ⊥ LN KO ⊥ JK ⇒ JR – расстояние между MI и JK,а KO – расстояние между LN и JK. При преломлении луча его часть JK ниже чем MI и LN на JR и KO соответственно. Если JR = KO, то LN являются продолжением MI. Пусть a∩FE=S и d∩GH=Z. Рассмотрим ⊿ RIJ – прямоугольный. ∠ RIJ=180 ° - ∠ AIS - ∠ SIJ - ∠ BIR. ∠ SIJ= α2. ∠ BAD= ∠ BIR=β так как соответственные углы при IR ∥ AD и секущей BA. ∠ AIS=90 ° так как угол между перпендикуляром a и отрезком BA. ∠ RIJ = 180 ° - 90 ° - α2 - β =90 ° - α2 - β . Рассмотрим ⊿ KOL – прямоугольный. ∠ OLK = 180 - ∠ ZLD - ∠ KLZ - ∠ OLC. ∠ OLC = β так как соответственные углы при OL ∥ AD и секущей CD. ∠ ZLD = 90 ° так как угол между перпендикуляром d и отрезком CD. ∠ KLZ = α2. ∠ OLK = 180 ° - 90 ° - α2 - β = 90 ° - α2 - β. ∠ OLK = ∠ RIJ = 90 ° - α2 - β. ⊿ RIJ подобен ⊿ KOL так как ∠ OLK = ∠ RIJ ⇒ ∠ OKL = ∠ RJI. Рассмотрим ⊿ SIJ и ⊿ LKZ – прямоугольные, имеют углы α2 и равные стороны IS и ZL заключённые между прямыми углами и углами α2. IS = ZL так как перпендикулярны боковым сторонам трапеций и, значит являются толщиной стенки колбы, которая одинаковая по условию. Следовательно ⊿ SIJ = ⊿ LKZ ⇒ IJ = KL. ⊿ RIJ = ⊿ KOL так как имеют равные отрезки KL и IJ заключённые между ∠ OLK = ∠ RIJ и ∠ OKL = ∠ RJI соответственно. JR = KO так как ⊿ RIJ = ⊿ KOL ⇒ LN является продолжением MI ч.т.д.

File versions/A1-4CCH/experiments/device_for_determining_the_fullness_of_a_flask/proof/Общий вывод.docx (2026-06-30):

После преломлений луча в пустой конической колбе, проходящего через ось вращения колбы и параллельно плоскости дна, он выйдет на таком же расстоянии от дна колбы, на котором и входил. После преломлений луча в наполненной конической колбе, проходящего через ось вращения колбы и параллельно плоскости дна, он будет направлен вниз. На фоторезистор попадает луч лазера только если колба пуста.

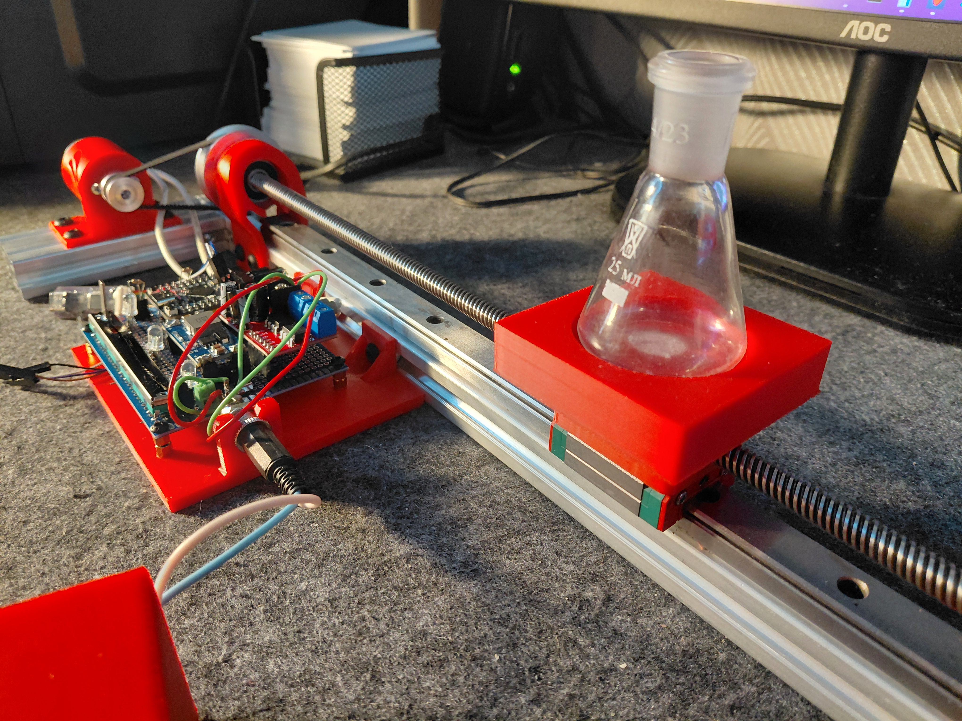
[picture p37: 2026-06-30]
versions/A2-4CCH/experiments/Pivot axis v1.0/media/Pivot_3.jpg

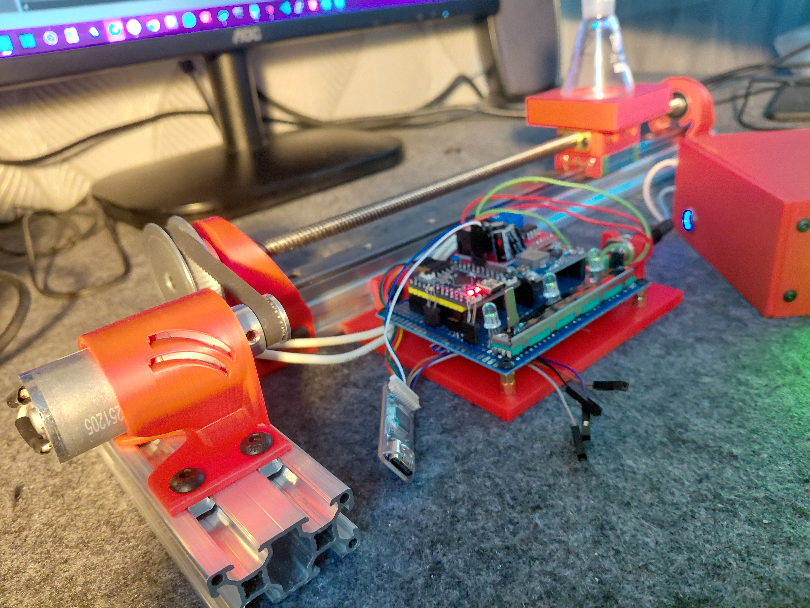
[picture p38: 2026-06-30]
versions/A2-4CCH/experiments/Pivot axis v1.0/media/Pivot_2.jpg

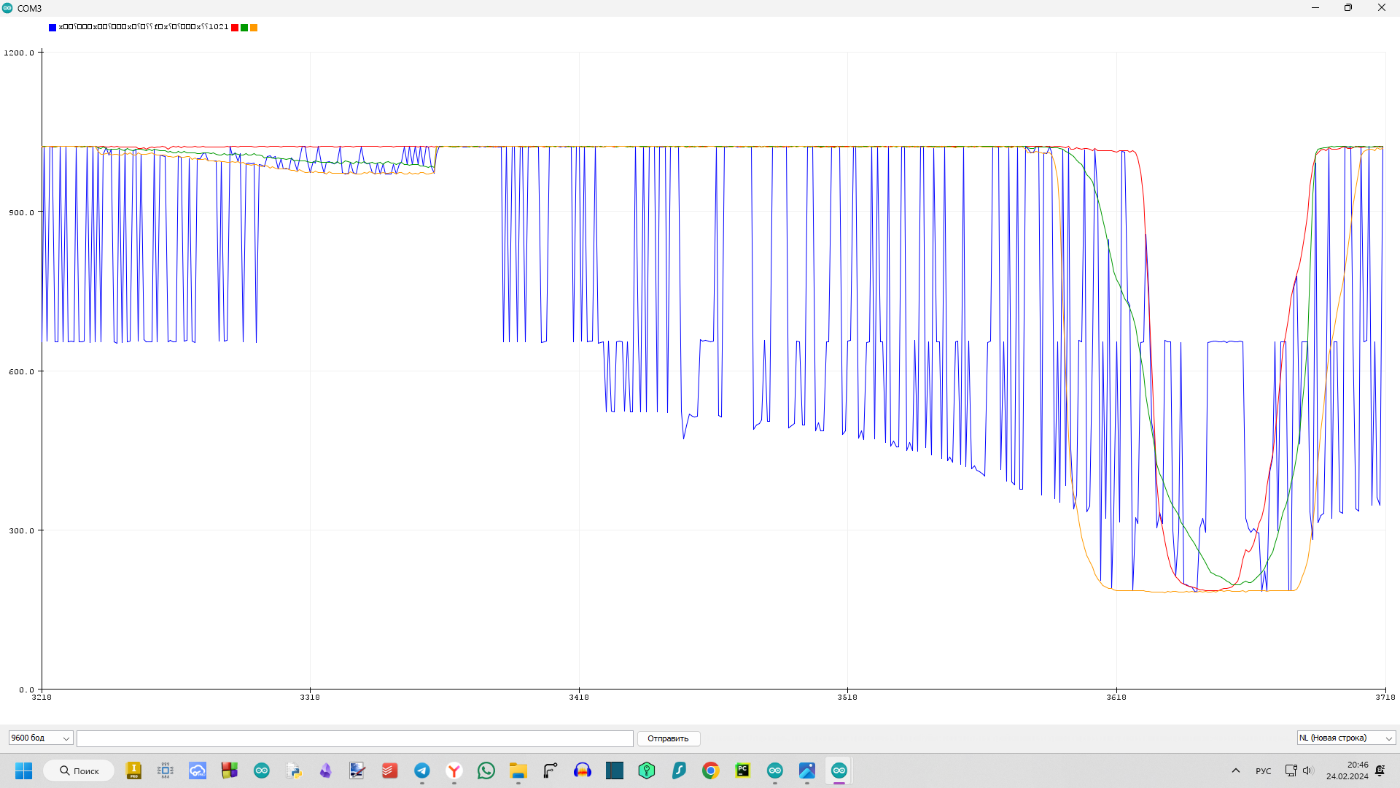
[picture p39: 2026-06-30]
versions/A1-4CCH/firmware/debugging/test_of_searching/Помехи и пустой отсек.png

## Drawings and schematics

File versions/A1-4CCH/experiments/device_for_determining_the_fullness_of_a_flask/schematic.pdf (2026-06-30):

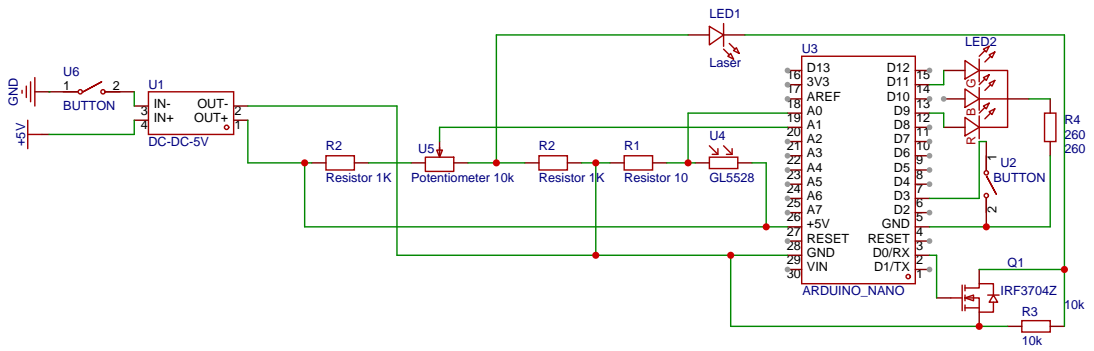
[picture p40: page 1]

D12 15 D13 16 3V3 17 AREF 18 A0 19 A1 20 A2 21 A3 22 A4 23 A5 24 A6 25 A7 26 +5V 27 RESET 28 GND 29 VIN 30

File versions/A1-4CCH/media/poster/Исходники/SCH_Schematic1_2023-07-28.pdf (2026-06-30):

## R2GL5528

## U5DC⁻DC ⁵V

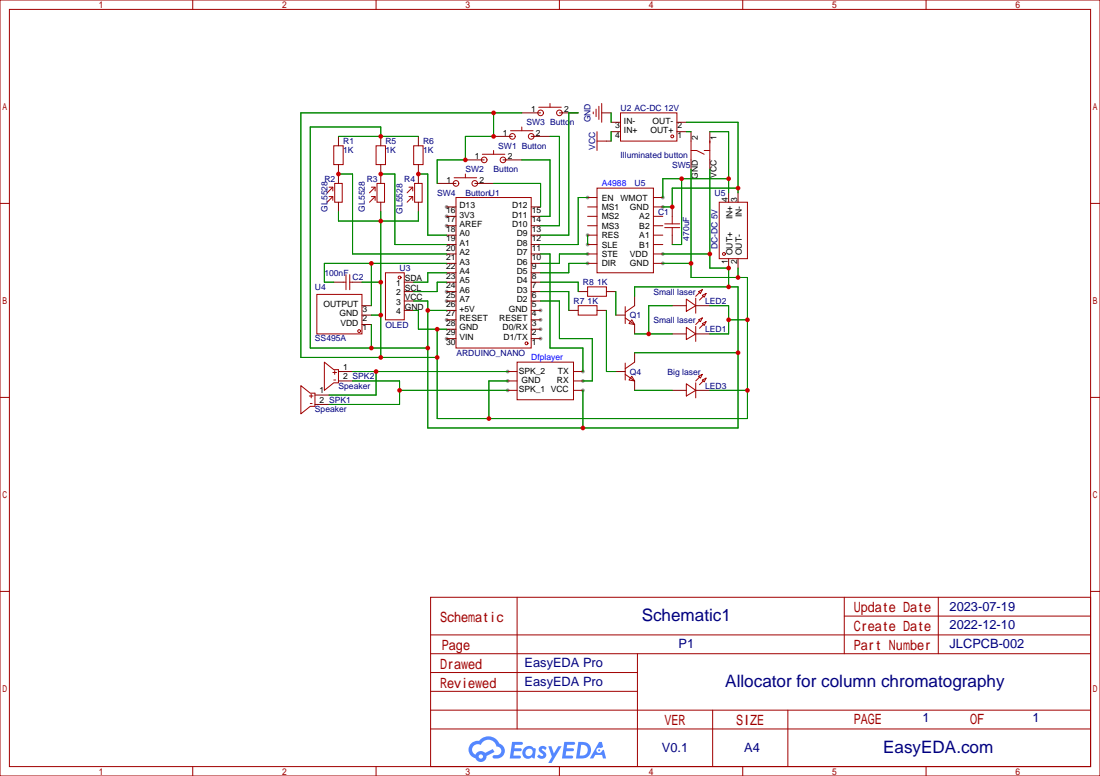
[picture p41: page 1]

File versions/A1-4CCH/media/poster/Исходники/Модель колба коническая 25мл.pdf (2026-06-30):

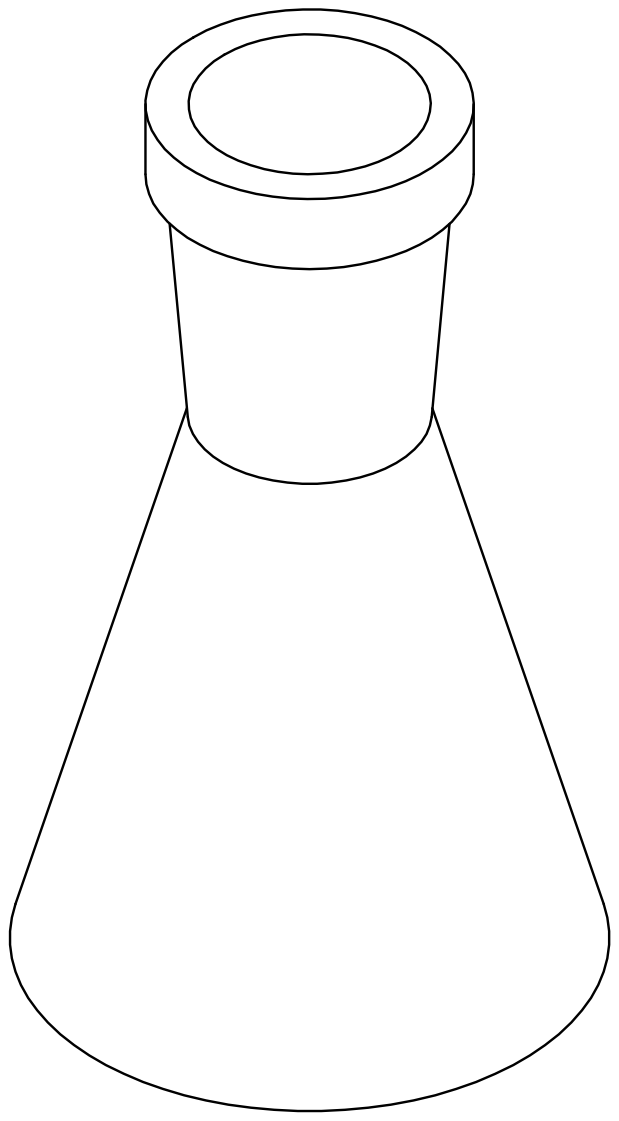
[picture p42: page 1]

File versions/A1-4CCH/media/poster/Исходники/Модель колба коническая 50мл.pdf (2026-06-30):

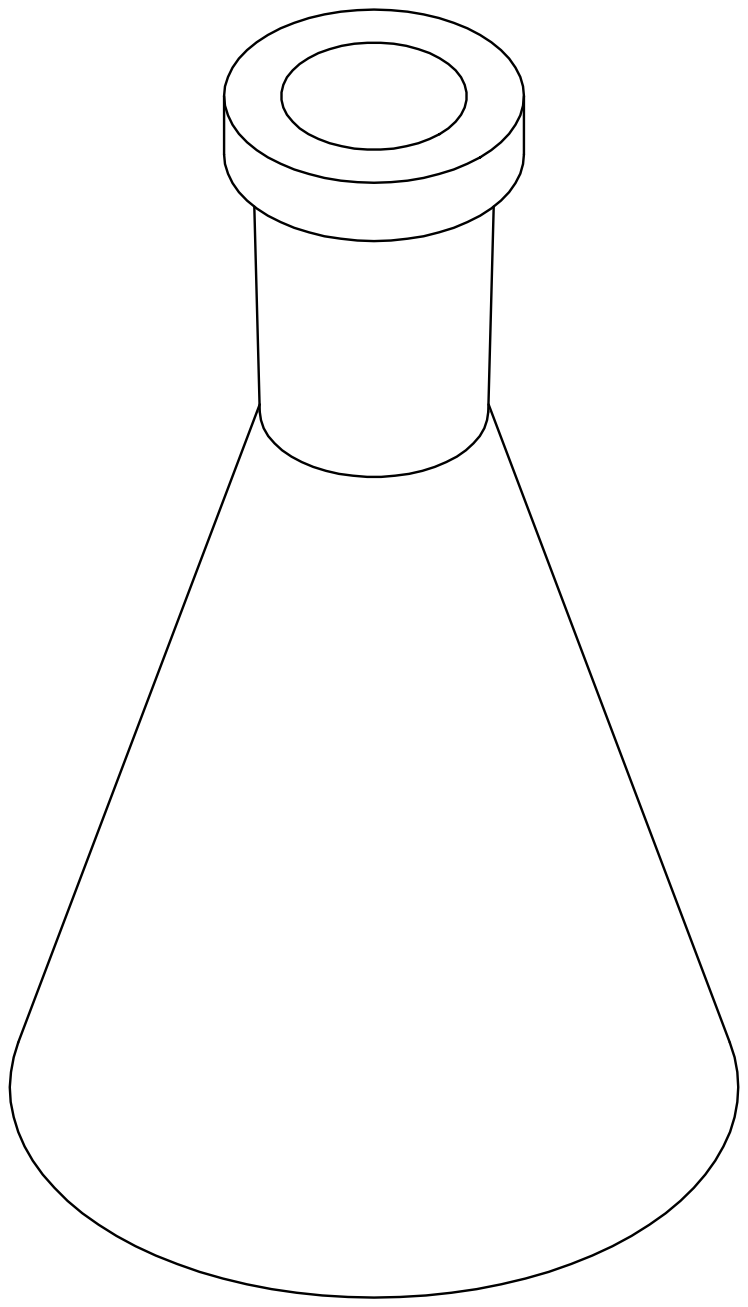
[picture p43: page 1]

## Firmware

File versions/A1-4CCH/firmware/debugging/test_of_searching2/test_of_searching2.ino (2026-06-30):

#define H_SPEED 2400
#define M_SPEED 3000
#define S_SPEED 15000
#define L_PHOTORESISTOR_TRESHOLD 700
#define R_PHOTORESISTOR_TRESHOLD 400
#define U_PHOTORESISTOR_TRESHOLD 600

#define BIG_LASER 3
#define SMALL_LASERS 4

#define R_PHOTORESISTOR A2
#define L_PHOTORESISTOR A1
#define U_PHOTORESISTOR A0
#define HOLL_SENSOR A3

#define PIN_DIR 5
#define PIN_STEP 6
#define SWITCH_OFF 8

int Min_U = 1023;
int New_U = 1023;
int Min_R = 1023;
int Min_L = 1023;
int New_R = 1023;
int New_L = 1023;

bool pos_flag = false;

uint32_t steper;

void setup() {
  pinMode(BIG_LASER, OUTPUT);
  pinMode(SMALL_LASERS, OUTPUT);
  pinMode(PIN_DIR, OUTPUT);
  pinMode(PIN_STEP, OUTPUT);

  pinMode(L_PHOTORESISTOR, INPUT);
  pinMode(R_PHOTORESISTOR, INPUT);
  pinMode(U_PHOTORESISTOR, INPUT);
  pinMode(HOLL_SENSOR, INPUT);
  pinMode(SWITCH_OFF, OUTPUT);
  digitalWrite(SWITCH_OFF, HIGH);

  digitalWrite(BIG_LASER, HIGH);
  digitalWrite(SMALL_LASERS, HIGH);
  pinMode(13, OUTPUT);
  digitalWrite(13, HIGH);
      digitalWrite(SWITCH_OFF, HIGH);

  Serial.begin(9600);
  steper = micros();
}

void loop() {
  for (;;) {
    if (micros() - steper >= M_SPEED) { //Средний шаг
      digitalWrite(PIN_STEP, HIGH);
    }
    if (micros() - steper >= M_SPEED * 2) {
      steper = micros();
      digitalWrite(PIN_STEP, LOW);
    }
    New_R = analogRead(R_PHOTORESISTOR);
    New_U = analogRead(U_PHOTORESISTOR);
    New_L = analogRead(L_PHOTORESISTOR);
    if (Min_L > New_L) {
      Min_L = New_L;
    }
    if (Min_R > New_R) {
      Min_R = New_R;
    }
    if (Min_U > New_U) {
      Min_U = New_U;
    }
    if (New_U - Min_U > 500) {
      Serial.print("Снятые показания: правый ");
      Serial.print(analogRead(R_PHOTORESISTOR));
      Serial.print(", левый ");
      Serial.print(analogRead(L_PHOTORESISTOR));
      Serial.print(", верхний ");
      Serial.print(analogRead(U_PHOTORESISTOR));
      Serial.println();
      Serial.print("Записанные показания: правый ");
      Serial.print(New_R);
      Serial.print(", левый ");
      Serial.print(New_L);
      Serial.print(", верхний ");
      Serial.print(New_U);
      Serial.println();
      Serial.print("Минимальные показания: правый ");
      Serial.print(Min_R);
      Serial.print(", левый ");
      Serial.print(Min_L);
      Serial.print(", верхний ");
      Serial.print(Min_U);
      Serial.println();
      pos_flag = true;
      if (Min_R < 350 and Min_L < 350 and Min_U < 300) {
        Serial.print("Пустой отсек");
        Serial.println();
        Serial.println();
      } else if (Min_R > 350) {
        Serial.print("Малая колба");
        Serial.println();
        Serial.println();
        delay(10000);
      } else {
        Serial.print("Большая колба");
        Serial.println();
        Serial.println();
        delay(10000);
      }
      Min_U = 1023;
      Min_R = 1023;
      Min_L = 1023;
      digitalWrite(SWITCH_OFF, HIGH);
      digitalWrite(SWITCH_OFF, LOW);
      for (int p = 0;;) {
        if (micros() - steper >= M_SPEED) {
          p++;
          steper = micros();
          if (p % 2 == 0) {
            digitalWrite(PIN_STEP, HIGH);
          } else {
            digitalWrite(PIN_STEP, LOW);
          }
          if (p > 1000) {
            break;
          }
        }
      }
    }
  }
  Serial.print(',');

}

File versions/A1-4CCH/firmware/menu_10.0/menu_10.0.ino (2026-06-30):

#include <GyverOLED.h>          // Библиотека дисплея
#include <EncButton2.h>         // Библиотека кнопок
#include <EEPROM.h>             // Библиотека управления EEPROM
#include "SoftwareSerial.h"
#include "DFRobotDFPlayerMini.h"
#include "Arduino.h"
#define OLED_SOFT_BUFFER_64  // Буфер на стороне МК

#define ITEMS 5
#define ITEMS2 3
#define ITEMS3 3
#define ITEMS4 3
#define ITEMS5 5

#define EB_DEB 50       // дебаунс кнопки, мс
#define EB_CLICK 50// таймаут накликивания кнопки, 

#define L_PHOTORESISTOR_TRESHOLD 700
#define R_PHOTORESISTOR_TRESHOLD 400
#define U_PHOTORESISTOR_TRESHOLD 600
#define HOLL_TRESHOLD 420

#define SPEED 3000

#define BIG_LASER 3
#define SMALL_LASERS 4
#define PIN_DIR 5
#define PIN_STEP 6
#define SWITCH_OFF 8
#define R_PHOTORESISTOR A2
#define L_PHOTORESISTOR A1
#define U_PHOTORESISTOR A0
#define HOLL_SENSOR A3

DFRobotDFPlayerMini myDFPlayer;
SoftwareSerial mySoftwareSerial(2, 7); // RX, TX


EncButton2<EB_BTN> btn[4];      // инициализация кнопок

EncButton2<EB_BTN> back(INPUT_PULLUP, 10);
EncButton2<EB_BTN> ok(INPUT_PULLUP, 9);
EncButton2<EB_BTN> down(INPUT_PULLUP, 12);
EncButton2<EB_BTN> up(INPUT_PULLUP, 11);

GyverOLED<SSD1306_128x64, OLED_BUFFER> oled;

void Launch();                  // Функция запуска сортировки
void Settings();                // Функция перехода в настройки
void BetterCallMe();            // Функция перехода в обратную связь
void Calibration();             // Функция перехода в раздел калибровки колб
void Sound();                   // Функция перехода в раздел изменения звука
void F25ml();                   // Функция перехода в раздел калибровки колбы 25 мл
void F50ml();                   // Функция перехода в раздел калибровки колбы 50 мл
void Logo();                    // Функция запуска анимации
void Mods();                    // Функция перехода в раздел с дополнениями
void Loud();                    // Функция перехода в раздел изменения громкости
void Succes();
void WatchFlask();
void df_step();
void Waiter();
void Base();
void Amongus();
void PoleChydes();



const uint8_t bitmap_127x27[] PROGMEM = { //Битмап логотипа без буквы
  0x00, 0x00, 0x00, 0x00, 0x00, 0x00, 0x00, 0x02, 0x06, 0x04, 0x84, 0x68, 0x18, 0x10, 0x30, 0x20, 0x40, 0xC0, 0x80, 0x80, 0x00, 0x00, 0x00, 0x00, 0x00, 0x00, 0x00, 0xC0, 0x60, 0x18, 0x0E, 0x03, 0x02, 0x02, 0x04, 0x04, 0x08, 0x18, 0x13, 0x32, 0x24, 0x44, 0xC8, 0x98, 0x90, 0x30, 0x20, 0x40, 0xC0, 0x00, 0x00, 0x00, 0xC0, 0x30, 0x1C, 0x06, 0x03, 0x02, 0x06, 0x04, 0x0C, 0x08, 0x10, 0x10, 0x08, 0x0C, 0x04, 0x06, 0x02, 0x03, 0x06, 0x1C, 0x30, 0xC0, 0x80, 0x00, 0x00, 0xC0, 0x40, 0x20, 0x20, 0x90, 0x90, 0xC8, 0x4C, 0x24, 0x26, 0x12, 0x10, 0x08, 0x0C, 0x04, 0x06, 0x02, 0x00, 0x00, 0x00, 0x00, 0x02, 0x0C, 0x38, 0x60, 0x80, 0x00, 0x00, 0x00, 0x00, 0x00, 0x00, 0x00, 0x00, 0x00, 0x00, 0x00, 0x00, 0x00, 0x00, 0x00, 0x00, 0x00, 0x00, 0x00, 0x00, 0x00, 0x00, 0x00, 0x00,
  0x00, 0x00, 0x00, 0x00, 0x00, 0x80, 0xE0, 0x30, 0x0C, 0x0F, 0x19, 0x70, 0xC0, 0x00, 0x00, 0x00, 0x00, 0x00, 0x80, 0xC1, 0x31, 0x1E, 0x86, 0x60, 0x30, 0x0C, 0x03, 0x01, 0x00, 0x00, 0x00, 0x00, 0x00, 0x00, 0x00, 0x00, 0x00, 0x00, 0x00, 0x00, 0xC0, 0x60, 0x18, 0x86, 0xE3, 0x30, 0x0C, 0xC7, 0x61, 0x18, 0x0E, 0x03, 0x01, 0x00, 0x00, 0x00, 0x00, 0x00, 0x00, 0x00, 0x00, 0x00, 0x00, 0x00, 0x00, 0x00, 0x00, 0x00, 0x00, 0x00, 0x00, 0x00, 0x00, 0x00, 0x03, 0x0E, 0x18, 0x60, 0xC7, 0x0C, 0x30, 0xE1, 0x87, 0x1C, 0x30, 0xC0, 0x80, 0x00, 0x00, 0x80, 0xC0, 0x40, 0x60, 0x20, 0x10, 0x10, 0x08, 0x0C, 0x04, 0x06, 0x00, 0x00, 0x01, 0x07, 0x0C, 0x30, 0xC0, 0x80, 0x00, 0x00, 0x00, 0x00, 0x00, 0x00, 0x00, 0x00, 0x00, 0x00, 0x00, 0x00, 0x00, 0x00, 0x00, 0x00, 0x00, 0x00, 0x00,
  0x00, 0xC0, 0x30, 0x1C, 0x06, 0x01, 0x00, 0x00, 0x00, 0x00, 0x00, 0x00, 0x00, 0x03, 0x0C, 0x38, 0x78, 0x86, 0x03, 0x00, 0x04, 0x0E, 0x09, 0x18, 0x10, 0x20, 0x60, 0x40, 0xC0, 0x80, 0x00, 0x00, 0x00, 0x00, 0x00, 0x80, 0x60, 0x38, 0x0C, 0x03, 0x01, 0x08, 0x1E, 0x31, 0x20, 0x40, 0x43, 0x81, 0x80, 0x00, 0x00, 0x00, 0x00, 0x00, 0x00, 0x00, 0x00, 0x00, 0x00, 0x00, 0x00, 0x00, 0x00, 0x00, 0x00, 0x00, 0x00, 0x00, 0x00, 0x00, 0x00, 0x00, 0x00, 0x00, 0x00, 0x00, 0x00, 0x80, 0x81, 0x43, 0x40, 0x20, 0x21, 0x17, 0x1C, 0x00, 0x03, 0x07, 0x19, 0x60, 0xC0, 0x00, 0x00, 0x00, 0x00, 0x00, 0x80, 0x80, 0x40, 0x60, 0x20, 0x30, 0x10, 0x08, 0x08, 0x00, 0x00, 0x03, 0x06, 0x18, 0x70, 0xC0, 0x00, 0x00, 0x00, 0x00, 0x00, 0x80, 0x80, 0x40, 0x60, 0x20, 0x30, 0x10, 0x18, 0x08, 0x08,
  0x03, 0x00, 0x00, 0x00, 0x00, 0x00, 0x00, 0x00, 0x00, 0x00, 0x00, 0x00, 0x00, 0x00, 0x00, 0x00, 0x00, 0x01, 0x03, 0x00, 0x00, 0x00, 0x00, 0x00, 0x00, 0x00, 0x00, 0x00, 0x00, 0x00, 0x01, 0x01, 0x02, 0x02, 0x03, 0x01, 0x00, 0x00, 0x00, 0x00, 0x00, 0x00, 0x00, 0x00, 0x00, 0x00, 0x00, 0x00, 0x01, 0x01, 0x03, 0x02, 0x04, 0x00, 0x00, 0x00, 0x00, 0x00, 0x00, 0x00, 0x00, 0x00, 0x00, 0x00, 0x00, 0x00, 0x00, 0x00, 0x00, 0x00, 0x00, 0x00, 0x00, 0x00, 0x02, 0x03, 0x01, 0x01, 0x00, 0x00, 0x00, 0x00, 0x00, 0x00, 0x00, 0x00, 0x00, 0x00, 0x00, 0x00, 0x01, 0x03, 0x06, 0x02, 0x03, 0x01, 0x00, 0x00, 0x00, 0x00, 0x00, 0x00, 0x00, 0x00, 0x00, 0x00, 0x00, 0x00, 0x00, 0x00, 0x00, 0x00, 0x03, 0x06, 0x02, 0x03, 0x01, 0x01, 0x00, 0x00, 0x00, 0x00, 0x00, 0x00, 0x00, 0x00, 0x00,
};
const uint8_t bitmap_16x19[] PROGMEM = {  //Битмап буквы логотипа
  0xFF, 0x00, 0x00, 0x00, 0x00, 0x00, 0x00, 0x00, 0x00, 0x00, 0x00, 0x00, 0x00, 0x00, 0x00, 0xFF,
  0xFF, 0x00, 0x00, 0x00, 0x00, 0x00, 0x00, 0x00, 0x00, 0x00, 0x00, 0x00, 0x00, 0x00, 0x00, 0xFF,
  0x03, 0x06, 0x04, 0x04, 0x04, 0x04, 0x04, 0x04, 0x04, 0x04, 0x04, 0x04, 0x04, 0x04, 0x04, 0x07,
};
const uint8_t bitmap_26x26_min[] PROGMEM = {  //Битмап знака минус
  0x00, 0x00, 0x00, 0x00, 0x00, 0x00, 0x00, 0x00, 0x00, 0x00, 0x00, 0x00, 0x00, 0x00, 0x00, 0x00, 0x00, 0x00, 0x00, 0x00, 0x00, 0x00, 0x00, 0x00, 0x00, 0x00,
  0x00, 0x00, 0x78, 0xFC, 0xFE, 0xFE, 0xFE, 0xFE, 0xFE, 0xFE, 0xFE, 0xFE, 0xFE, 0xFE, 0xFE, 0xFE, 0xFE, 0xFE, 0xFE, 0xFE, 0xFE, 0xFE, 0xFC, 0x78, 0x00, 0x00,
  0x00, 0x00, 0x00, 0x00, 0x01, 0x01, 0x01, 0x01, 0x01, 0x01, 0x01, 0x01, 0x01, 0x01, 0x01, 0x01, 0x01, 0x01, 0x01, 0x01, 0x01, 0x01, 0x00, 0x00, 0x00, 0x00,
  0x00, 0x00, 0x00, 0x00, 0x00, 0x00, 0x00, 0x00, 0x00, 0x00, 0x00, 0x00, 0x00, 0x00, 0x00, 0x00, 0x00, 0x00, 0x00, 0x00, 0x00, 0x00, 0x00, 0x00, 0x00, 0x00,
};
const uint8_t bitmap_26x26_plus[] PROGMEM = { //Битмап знака плюс
  0x00, 0x00, 0x00, 0x00, 0x00, 0x00, 0x00, 0x00, 0x00, 0xFC, 0xFC, 0xFC, 0xFC, 0xFC, 0xFC, 0xFC, 0xFC, 0x00, 0x00, 0x00, 0x00, 0x00, 0x00, 0x00, 0x00, 0x00,
  0x00, 0x00, 0xFE, 0xFE, 0xFE, 0xFE, 0xFE, 0xFE, 0xFE, 0xFF, 0xFF, 0xFF, 0xFF, 0xFF, 0xFF, 0xFF, 0xFF, 0xFE, 0xFE, 0xFE, 0xFE, 0xFE, 0xFE, 0xFE, 0x00, 0x00,
  0x00, 0x00, 0x01, 0x01, 0x01, 0x01, 0x01, 0x01, 0x01, 0xFF, 0xFF, 0xFF, 0xFF, 0xFF, 0xFF, 0xFF, 0xFF, 0x01, 0x01, 0x01, 0x01, 0x01, 0x01, 0x01, 0x00, 0x00,
  0x00, 0x00, 0x00, 0x00, 0x00, 0x00, 0x00, 0x00, 0x00, 0x00, 0x00, 0x00, 0x00, 0x00, 0x00, 0x00, 0x00, 0x00, 0x00, 0x00, 0x00, 0x00, 0x00, 0x00, 0x00, 0x00,
};
const uint8_t bitmap_128x64_colba[] PROGMEM = {//Битмап хроматографии
  0x00, 0x00, 0x00, 0x00, 0x00, 0x00, 0x00, 0x00, 0x00, 0x00, 0x00, 0x00, 0x00, 0x00, 0x00, 0x00, 0x00, 0x00, 0x00, 0x00, 0x00, 0x00, 0x00, 0x00, 0x00, 0x00, 0x00, 0x00, 0x00, 0x00, 0x00, 0x00, 0x00, 0x00, 0x00, 0x00, 0x00, 0x00, 0x00, 0x00, 0x00, 0x00, 0x00, 0x00, 0x00, 0x00, 0x00, 0x00, 0x00, 0x00, 0x00, 0x00, 0x00, 0x00, 0x00, 0x00, 0x00, 0x00, 0xFF, 0xFF, 0xAB, 0xFF, 0xAB, 0x7F, 0xEB, 0x5F, 0xFB, 0x57, 0xFF, 0xFF, 0x00, 0x00, 0x00, 0x00, 0x00, 0x00, 0x00, 0x00, 0x00, 0x00, 0x00, 0x00, 0x00, 0x00, 0x00, 0x00, 0x00, 0x00, 0x00, 0x00, 0x00, 0x00, 0x00, 0x00, 0x00, 0x00, 0x00, 0x00, 0x00, 0x00, 0x00, 0x00, 0x00, 0x00, 0x00, 0x00, 0x00, 0x00, 0x00, 0x00, 0x00, 0x00, 0x00, 0x00, 0x00, 0x00, 0x00, 0x00, 0x00, 0x00, 0x00, 0x00, 0x00, 0x00, 0x00, 0x00, 0x00, 0x00,
  0x00, 0x00, 0x00, 0x00, 0x00, 0x00, 0x00, 0x00, 0x00, 0x00, 0x00, 0x00, 0x00, 0x00, 0x00, 0x00, 0x00, 0x00, 0x00, 0x00, 0x00, 0x00, 0x00, 0x00, 0x00, 0x00, 0x00, 0x00, 0x00, 0x00, 0x00, 0x00, 0x00, 0x00, 0x00, 0x00, 0x00, 0x00, 0x00, 0x00, 0x00, 0x00, 0x00, 0x00, 0x00, 0x00, 0x00, 0x00, 0x00, 0x00, 0x00, 0x00, 0x00, 0x00, 0x00, 0x00, 0x00, 0x00, 0x07, 0x0F, 0x1A, 0x7D, 0xF7, 0xFD, 0xEB, 0xFD, 0x17, 0x1D, 0x0F, 0x07, 0x00, 0x00, 0x00, 0x00, 0x00, 0x00, 0x00, 0x00, 0x00, 0x00, 0x00, 0x00, 0x00, 0x00, 0x00, 0x00, 0x00, 0x00, 0x00, 0x00, 0x00, 0x00, 0x00, 0x00, 0x00, 0x00, 0x00, 0x00, 0x00, 0x00, 0x00, 0x00, 0x00, 0x00, 0x00, 0x00, 0x00, 0x00, 0x00, 0x00, 0x00, 0x00, 0x00, 0x00, 0x00, 0x00, 0x00, 0x00, 0x00, 0x00, 0x00, 0x00, 0x00, 0x00, 0x00, 0x00, 0x00, 0x00,
  0x00, 0x00, 0x00, 0x00, 0x00, 0x00, 0x00, 0x00, 0x00, 0x00, 0x00, 0x00, 0x00, 0x00, 0x00, 0x00, 0x00, 0x00, 0x00, 0x00, 0x00, 0x00, 0x00, 0x00, 0x00, 0x00, 0x00, 0x00, 0x00, 0x00, 0x00, 0x00, 0x00, 0x00, 0x00, 0x00, 0x00, 0x00, 0x00, 0x00, 0x00, 0x00, 0x00, 0x00, 0x00, 0x00, 0x00, 0x00, 0x00, 0x00, 0x00, 0x00, 0x00, 0x00, 0x00, 0x00, 0x00, 0x00, 0x00, 0x00, 0x1C, 0x1C, 0x7F, 0xFF, 0xFF, 0xFF, 0x1C, 0x1C, 0x00, 0x00, 0x00, 0x00, 0x00, 0x00, 0x00, 0x00, 0x00, 0x00, 0x00, 0x00, 0x00, 0x00, 0x00, 0x00, 0x00, 0x00, 0x00, 0x00, 0x00, 0x00, 0x00, 0x00, 0x00, 0x00, 0x00, 0x00, 0x00, 0x00, 0x00, 0x00, 0x00, 0x00, 0x00, 0x00, 0x00, 0x00, 0x00, 0x00, 0x00, 0x00, 0x00, 0x00, 0x00, 0x00, 0x00, 0x00, 0x00, 0x00, 0x00, 0x00, 0x00, 0x00, 0x00, 0x00, 0x00, 0x00, 0x00, 0x00,
  0x00, 0x00, 0x00, 0x00, 0x00, 0x00, 0x00, 0x00, 0x00, 0x00, 0x00, 0x00, 0x00, 0x00, 0x00, 0x00, 0x00, 0x00, 0x00, 0x00, 0x00, 0x00, 0x00, 0x00, 0x00, 0x00, 0x00, 0x00, 0x00, 0x00, 0x00, 0x00, 0x00, 0x00, 0x00, 0x00, 0x00, 0x00, 0x00, 0x00, 0x00, 0x00, 0x00, 0x00, 0x00, 0x00, 0x00, 0x00, 0x00, 0x00, 0x00, 0x00, 0x00, 0x00, 0x00, 0x00, 0x00, 0x00, 0x00, 0x00, 0x00, 0x00, 0x00, 0x00, 0x01, 0x03, 0x00, 0x00, 0x00, 0x00, 0x00, 0x00, 0x00, 0x00, 0x00, 0x00, 0x00, 0x00, 0x00, 0x00, 0x00, 0x00, 0x00, 0x00, 0x00, 0x00, 0x00, 0x00, 0x00, 0x00, 0x00, 0x00, 0x00, 0x00, 0x00, 0x00, 0x00, 0x00, 0x00, 0x00, 0x00, 0x00, 0x00, 0x00, 0x00, 0x00, 0x00, 0x00, 0x00, 0x00, 0x00, 0x00, 0x00, 0x00, 0x00, 0x00, 0x00, 0x00, 0x00, 0x00, 0x00, 0x00, 0x00, 0x00, 0x00, 0x00, 0x00, 0x00,
  0x00, 0x00, 0x00, 0x00, 0x00, 0x00, 0x00, 0x00, 0x00, 0x3F, 0xC1, 0x01, 0x01, 0x01, 0x01, 0xC1, 0x3F, 0x00, 0x00, 0x00, 0x00, 0x00, 0x00, 0x00, 0x00, 0x00, 0x00, 0x00, 0x00, 0x00, 0x00, 0x00, 0x00, 0x00, 0x00, 0x00, 0x00, 0x00, 0x00, 0x00, 0x00, 0x00, 0x00, 0x00, 0x00, 0x00, 0x00, 0x00, 0x00, 0x00, 0x00, 0x00, 0x00, 0x00, 0x00, 0x00, 0x00, 0x00, 0x00, 0x00, 0x1F, 0xE1, 0x01, 0x01, 0x01, 0x01, 0xE1, 0x1F, 0x00, 0x00, 0x00, 0x00, 0x00, 0x00, 0x00, 0x00, 0x00, 0x00, 0x00, 0x00, 0x00, 0x00, 0x00, 0x00, 0x00, 0x00, 0x00, 0x00, 0x00, 0x00, 0x00, 0x00, 0x00, 0x00, 0x00, 0x00, 0x00, 0x00, 0x00, 0x00, 0x00, 0x00, 0x00, 0x00, 0x00, 0x00, 0x00, 0x00, 0x00, 0x00, 0x1F, 0xE1, 0x01, 0x01, 0x01, 0x01, 0xE1, 0x1F, 0x00, 0x00, 0x00, 0x00, 0x00, 0x00, 0x00, 0x00, 0x00, 0x00,
  0x00, 0x00, 0x00, 0x00, 0x00, 0x00, 0x00, 0x00, 0xF0, 0x0E, 0x01, 0x00, 0x00, 0x00, 0x00, 0x01, 0x0E, 0xF0, 0x00, 0x00, 0x00, 0x00, 0x00, 0x00, 0x00, 0x00, 0x00, 0x00, 0x00, 0x00, 0x00, 0x00, 0x00, 0x00, 0x00, 0x00, 0x00, 0x00, 0x00, 0x00, 0x00, 0x00, 0x00, 0x00, 0x00, 0x00, 0x00, 0x00, 0x00, 0x00, 0x00, 0x00, 0x00, 0x00, 0x00, 0x00, 0x00, 0x00, 0xE0, 0x18, 0x07, 0x00, 0x00, 0x00, 0x00, 0x00, 0x00, 0x07, 0x18, 0xE0, 0x00, 0x00, 0x00, 0x00, 0x00, 0x00, 0x00, 0x00, 0x00, 0x00, 0x00, 0x00, 0x00, 0x00, 0x00, 0x00, 0x00, 0x00, 0x00, 0x00, 0x00, 0x00, 0x00, 0x00, 0x00, 0x00, 0x00, 0x00, 0x00, 0x00, 0x00, 0x00, 0x00, 0x00, 0x00, 0x00, 0x00, 0x00, 0xE0, 0xFC, 0xF3, 0xB0, 0xF0, 0xB0, 0xD0, 0xF0, 0xB0, 0xF3, 0xBC, 0xE0, 0x00, 0x00, 0x00, 0x00, 0x00, 0x00, 0x00, 0x00,
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
